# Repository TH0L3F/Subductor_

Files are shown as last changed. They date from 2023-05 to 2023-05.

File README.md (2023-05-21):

#Subductor

Une machine pour le laboratoire de sciences naturelles de L'université de Lille (Cité scientifique) SN5

## Objectif

Le subductor a pour objectif de subducter ... Bon c'est pas super clair comme ça donc je vais faire mieux:
L'objectif est de tirer un bloc de sable avec un tissus (ici un morceau de voile de bateau) par le dessous afin de simuler des mouvements tectoniques et leurs effets sur des blocs de sable.

### Matériel

Pour se faire est mis à la disposition de l'utilisateur un boitier possédant un écran lcd 4 lignes 20 caractères par lignes ainsi qu'un encodeur rotatif avec un bouton inclus.

### Préparation

Au démarrage de la machine il faut avec le mode Incrémental faire deux tours de aux tapis autour de la tige d'enroulement puis redemarrer la machine pour commencer à l'utiliser.
Le nombre d'enroulement du tapis n'étant pas mesurer : il s'agit de la seule manière de connaître sa position eu démarrage puis de la calculer au cours du fonctionnement de la machine.

### Mode

Dans un premier temps il faut choisir un mode entre:
-Continu : Sélection de la vitesse de déplacement du tapis.
-Incrémental : Sélection de la position voulue du tapis puis déplacement de celui-ci.

Pour passer d'un mode à l'autre il faut éteindre puis allumer la machine (Choix seulement au démarrage).

#### Continu

Choix de la vitesse avec l'encodeur puis appuie sur le bouton 2 secondes pour mettre en mouvement la machine.
Lors d'un changement de vitesse en bougeant l'encodeur il faut appuyer sur le bouton pour confirmer la modification et qu'elle devienne effective.

#### Incrémental

Choix de la position avec l'encodeur puis appuie sur le bouton 2 secondes pour mettre en mouvement la machine.
A chaques changement de position il faut appuyer à nouveau sur le bouton pendant 2 secondes sur le bouton de l'encodeur pour que le changement soit pris en compte.

## Electronique

Du point de vue électronique une carte permet de connecter chaques composants via des connecteurs JST-XH afin de limiter au maximum la possibilité de déconnexion dû aux vibrations ou au temps. Les composants sont tous connecter à un atmega328p cadencé à 16MHz. L'écran en I2C et l'encodeur sur des pin digital. Le driver de moteur pas à pas sur des pins digital lui aussi.

## Programmation

Pour programmer il faut utiliser un programmateur spécifique et le connecteur correspondant sur la carte. Le programmateur est le même que le programmateur du projet Slicor. Une petite fléche permet sur la carte et le connecteur du programmateur permet de détromper le sens de connexion. Ensuite via l'IDE arduino il est possible de mettre le bootloader ("carte : arduino uno", "programmateur : TINYasISP" puis "burn bootloader") il est nécessaire de mettre le bootloader si la puce n'en a pas déjà. Ensuite avec l'option "programmer via un programmateur" il est possible de téléverser le programmer dans le microcontrôleur. 

ATTENTION: Avec le programmeteur mis à dispositon une erreur survient dans certaine condition. Si un timeout est émis par le programmateur une solution est d'enlever ou d'ajouter des delay(1) dans la partie setup du programme. (Si une meilleure solution existe je suis preneur).

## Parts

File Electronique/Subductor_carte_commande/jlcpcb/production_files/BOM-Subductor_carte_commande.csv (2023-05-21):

Comment | Designator | Footprint | LCSC
16MHz | Y1 | Crystal_SMD_3225-4Pin_3.2x2.5mm | C13738
ATmega328-A | uC1 | TQFP-32_7x7mm_P0.8mm | C14877
22p | C3,C4 | C_0402_1005Metric | C1555
100k | R13 | R_1206_3216Metric | C17900
10k | R1,R2 | R_1206_3216Metric | C17902
Connecteur_Prog | J4 | PinHeader_1x08_P2.54mm_Vertical
Conn_encodeur_rotatif | J3 | JST_XH_B5B-XH-A_1x05_P2.50mm_Vertical
Connecteur_bouton_1 | J5 | JST_XH_B2B-XH-A_1x02_P2.50mm_Vertical
Connecteur_ecran | J2 | JST_XH_B4B-XH-A_1x04_P2.50mm_Vertical
Connecteur_Alim | J1 | TerminalBlock_bornier-2_P5.08mm
MountingHole_Pad | H1 | MountingHole_4.3mm_M4_DIN965_Pad
MountingHole_Pad | H4 | MountingHole_4.3mm_M4_DIN965_Pad
Connecteur_bouton_2 | J6 | JST_XH_B2B-XH-A_1x02_P2.50mm_Vertical
MountingHole_Pad | H3 | MountingHole_4.3mm_M4_DIN965_Pad
MountingHole_Pad | H2 | MountingHole_4.3mm_M4_DIN965_Pad
TestPoint | TP1 | TestPoint_Pad_1.5x1.5mm
Conn_01x03_Female | J7 | JST_XH_B3B-XH-A_1x03_P2.50mm_Vertical

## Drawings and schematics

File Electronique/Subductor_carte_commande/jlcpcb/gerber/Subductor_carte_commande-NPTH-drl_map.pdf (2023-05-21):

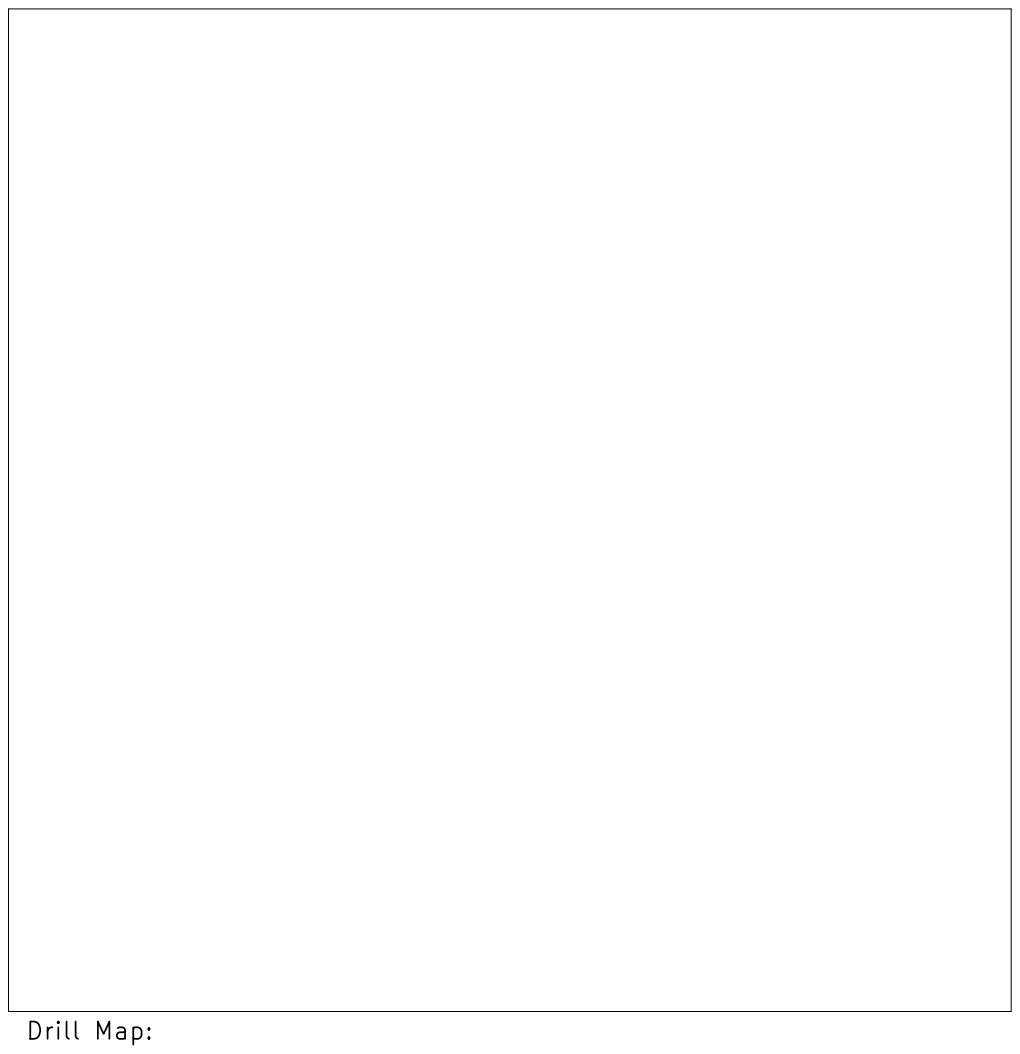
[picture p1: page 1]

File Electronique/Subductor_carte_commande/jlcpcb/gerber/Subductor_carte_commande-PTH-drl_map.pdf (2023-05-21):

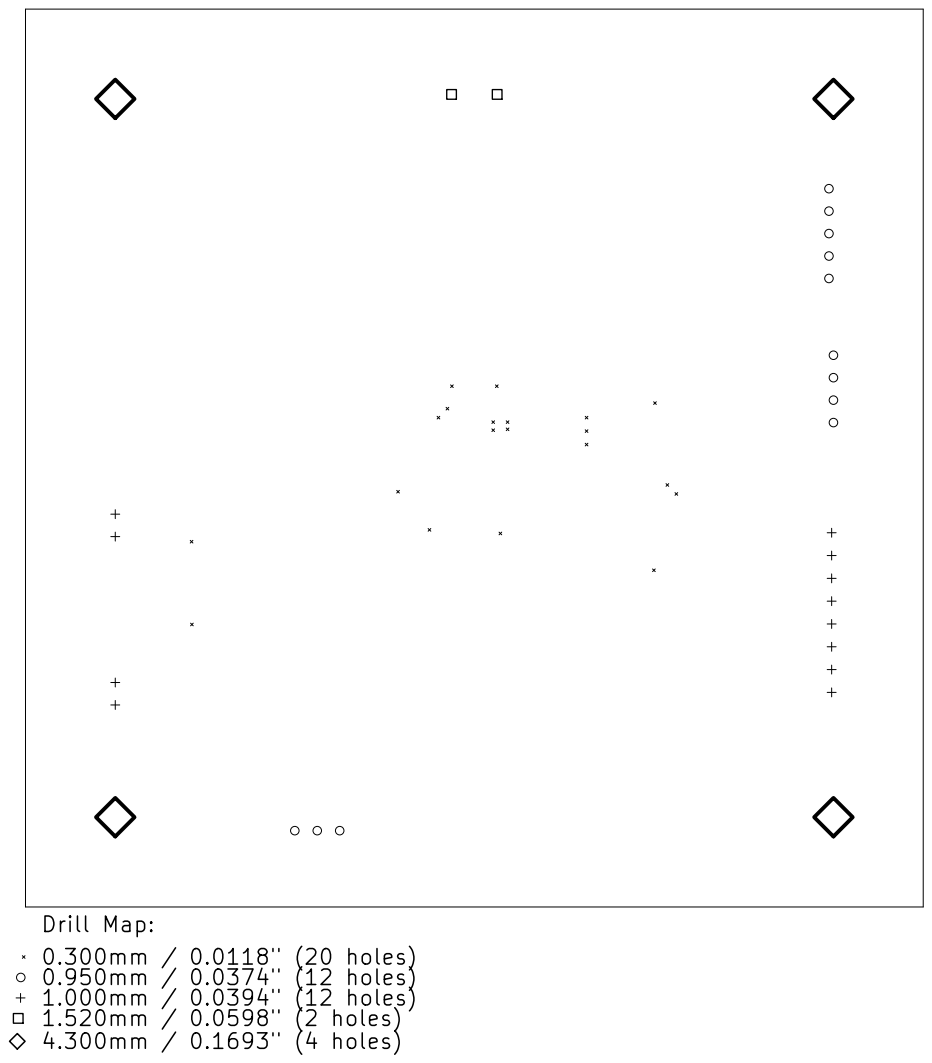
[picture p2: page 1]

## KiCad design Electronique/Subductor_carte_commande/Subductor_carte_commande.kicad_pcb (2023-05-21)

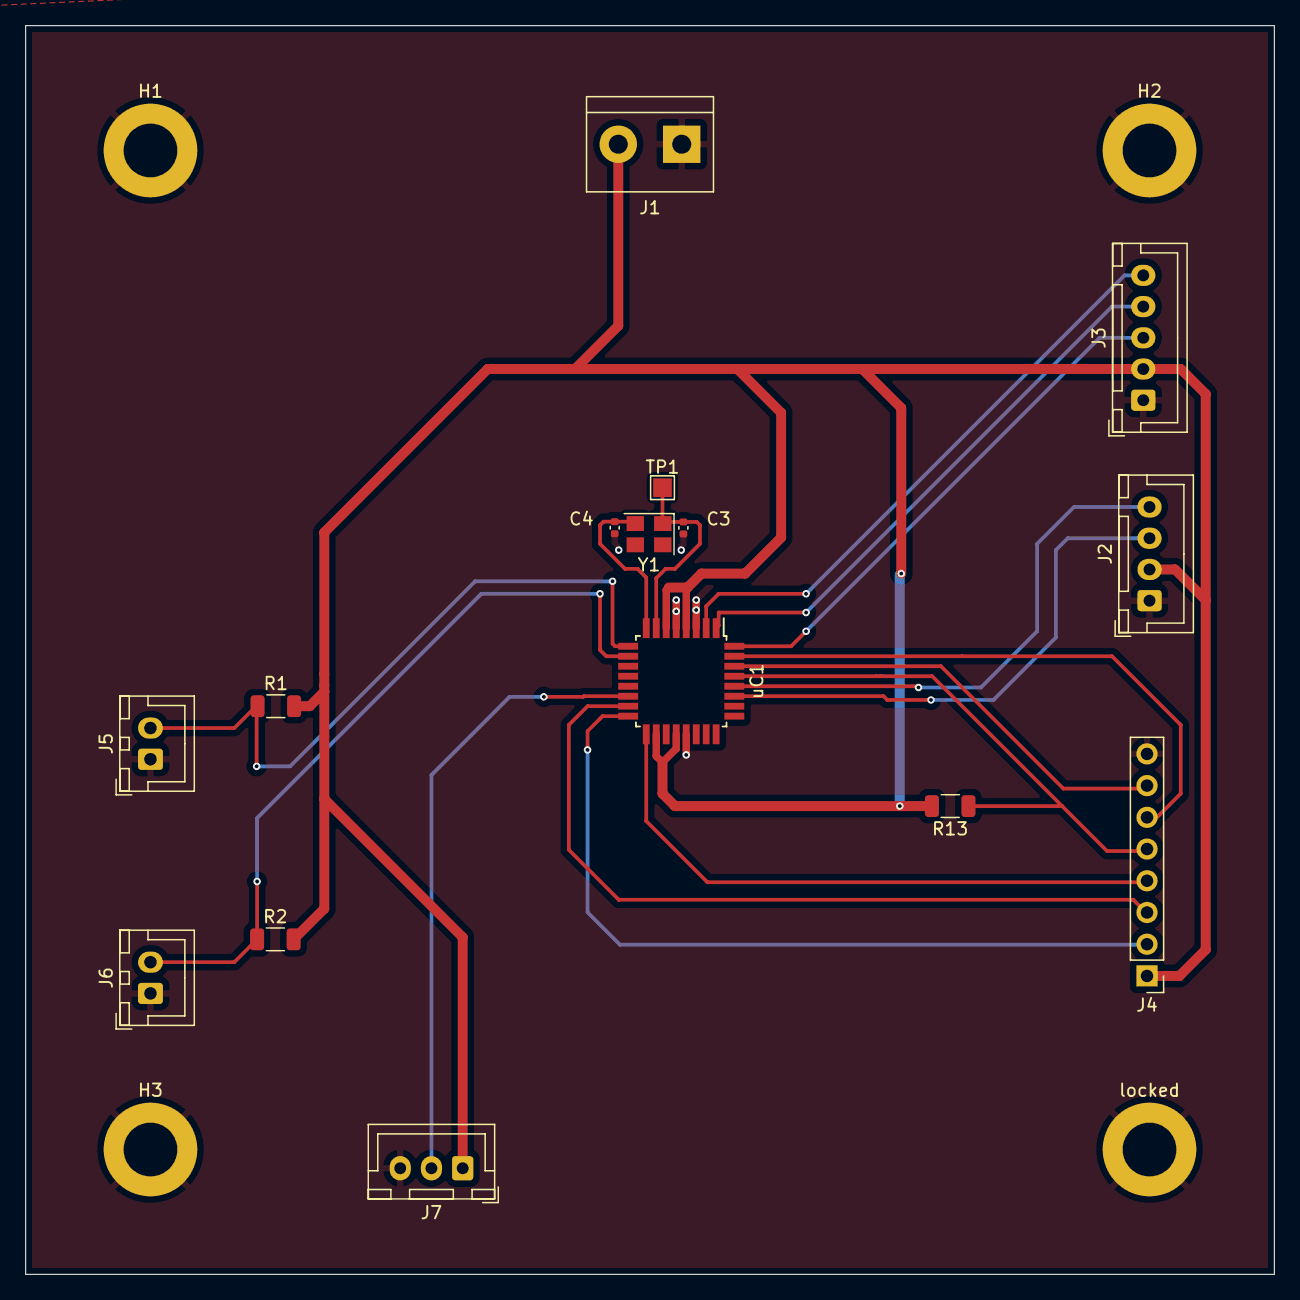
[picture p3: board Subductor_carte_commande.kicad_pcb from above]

Board: 4 copper layers, 100.0 x 100.0 mm, 19 parts (0 on the bottom side), 18 nets.

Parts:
C3, C4: 22p; C_0402_1005Metric
H1, H2, H3: MountingHole_Pad; MountingHole_4.3mm_M4_DIN965_Pad
J1: Connecteur_Alim; TerminalBlock_bornier-2_P5.08mm
J2: Connecteur_ecran; JST_XH_B4B-XH-A_1x04_P2.50mm_Vertical
J3: Conn_encodeur_rotatif; JST_XH_B5B-XH-A_1x05_P2.50mm_Vertical
J4: Connecteur_Prog; PinHeader_1x08_P2.54mm_Vertical
J5: Connecteur_bouton_1; JST_XH_B2B-XH-A_1x02_P2.50mm_Vertical
J6: Connecteur_bouton_2; JST_XH_B2B-XH-A_1x02_P2.50mm_Vertical
J7: Conn_01x03_Female; JST_XH_B3B-XH-A_1x03_P2.50mm_Vertical
R1, R2: 10k; R_1206_3216Metric
R13: 100k; R_1206_3216Metric
TP1: TestPoint; TestPoint_Pad_1.5x1.5mm
Y1: 16MHz; Crystal_SMD_3225-4Pin_3.2x2.5mm
locked: MountingHole_Pad; MountingHole_4.3mm_M4_DIN965_Pad
uC1: ATmega328-A; TQFP-32_7x7mm_P0.8mm

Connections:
+5V: J1.2, J2.2, J3.2, J4.1, J7.1, R1.2, R2.2, R13.2, uC1.4 (VCC), uC1.6 (VCC), uC1.18 (AVCC), uC1.20 (AREF)
BUZZER: J7.2, uC1.14 (PB2)
Bouton1: J5.2, R1.1, uC1.9 (PD5)
Bouton2: J6.2, R2.1, uC1.10 (PD6)
CLK: J3.5, uC1.2 (PD4)
DT: J3.4, uC1.1 (PD3)
GND: C3.2, C4.2, H1.1, H2.1, H3.1, J1.1, J2.1, J3.1, J4.8, J5.1, J6.1, J7.3, locked.1, uC1.3 (GND), uC1.5 (GND), uC1.21 (GND)
MISO: J4.2, uC1.16 (PB4)
MOSI: J4.3, uC1.15 (PB3)
unnamed: C3.1, TP1.1, Y1.1, uC1.7 (XTAL1/PB6)
unnamed: C4.1, Y1.2, uC1.8 (XTAL2/PB7)
RST: J4.5, R13.1, uC1.29 (~RESET/PC6)
SCK: J4.4, uC1.17 (PB5)
SCL: J2.4, uC1.28 (PC5)
SDA: J2.3, uC1.27 (PC4)
SW: J3.3, uC1.32 (PD2)
UART RX: J4.7, uC1.30 (PD0)
UART TX: J4.6, uC1.31 (PD1)

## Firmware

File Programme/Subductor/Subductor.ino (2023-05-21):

/*
Software by TH0L3F
*/

//Utilitaire pour l'écran LCD
#include <Wire.h> 
#include <LiquidCrystal_I2C.h>
#define len_lcd 20 //Nombre de caractère en longueur de l'écran
#define high_lcd 4 //Nombre de lignes de l'écran
#define lcd_adress 0x27 //Adresse de l'écran
LiquidCrystal_I2C lcd(lcd_adress,len_lcd,high_lcd);  //Configurer l'écran 
bool screen_refresh = false;

//Encodeur rotatif KY-040
//Parameters
#define CLK 2
#define DT 3
#define SW 4
int counter = 0;
bool pos_chng = 0;
unsigned long old_pos = 0; //Ancienne position du tapis en dizieme de um
unsigned long new_pos = 0; //Nouvelle position du tapis en dizieme de um
bool ax = false; //Ancien état de la broche A
bool bx = false; //Ancien état de la broche B
bool a = false; //Nouvel état de la broche A
bool b = false; //Nouvel état de la broche B
bool btn = 0;
bool abtn = 0;
unsigned long t1 = 0;
unsigned long t2 = 0;
unsigned long t3 = 0;

//Buzzer
#define pin_buzzer 10

//Driver stepper
#define DR_step 5 //Broche d'impulsion pour chaques pas
#define DR_dir 6 //Broche de sélection de la direction
const long step_per_revolution = 800; // Nombre de par par révolution du moteur pas à pas
const long init_r = 180000; //rayon initial de l'axe d'enroulement en en dizieme de um
const long red = 100; //Coefficient de réduction du moteur
long step_per_rev_red = step_per_revolution*red; //Nombre de pas du moteur pour faire un tour en sortie du réducteur
long e = 4000; //Epaisseur du tissus en en dizieme de um
long n_step_f = 0;//Enregistre le nombre de pas effectuer depuis le début du tour actuel
long n_tour = 2;//Enregistre le nombre de tour effectuer depuis le démarrage de la machine
unsigned long mm_step = 0;//Permet de sauvegarder le nombre de dizieme de um effectuer à chaques pas.
long pi =  31415; //Pi en dizieme de um
long delay_step = 100; //Temps d'attente entre deux pas.

//Choix de mode
bool mode = 0;  //Permet de sauvegarder le mode choisie au démarrage
                //0 mode incrémental
                //1 mode continue
int sel;//Sauvegarde de la position en cours
char c1;//Affichage du choix 
char c2;//Affichage du choix
char c3;//Affichage du choix

//Mode continue
#define v1 5 //5mm/h
#define v2 10 //10mm/h
int vitesse = 0; //Vitesse choisir au démarrage

void setup(){
  //Configurer l'éc&ran LCD
  lcd.init();  //initialize the lcd
  lcd.backlight();  //open the backlight 

  pinMode(CLK, INPUT_PULLUP);
  pinMode(DT, INPUT_PULLUP);
  attachInterrupt(digitalPinToInterrupt(CLK), readRotary, CHANGE);
  attachInterrupt(digitalPinToInterrupt(DT), readRotary, CHANGE);

  pinMode(SW, INPUT_PULLUP);

  pinMode(pin_buzzer, OUTPUT);

  pinMode(DR_step, OUTPUT);
  pinMode(DR_dir, OUTPUT);
  mm_step = (((e*n_tour+init_r)/red)*2*pi)/step_per_revolution/1000;

  //Affichage au démarrage
  screen(mode);
  delay(2000);
  screen(1);

  delay(1);
  delay(1);
  delay(1);
  delay(1);
  delay(1);
  delay(1);
  delay(1);
  delay(1);

}

void loop(){
  if(screen_refresh){
    screen(mode); //Mise à jour de l'écran
    screen_refresh = false;
  }
  if(pos_chng){
    if((mode == 2) || (mode == 3)){
      new_pos = (counter/4)*100000;
    }
    else if(mode == 1){
      sel = (counter/4)%3;
    }
    pos_chng = 0;
    screen_refresh = 1;

  }
  button();//Permet de récupérer les infos sur le bouton et d'executer les actions associés.
}

void button(){
  btn = digitalRead(SW);
  if((mode == 3)||(mode == 2)){
    if(abtn == HIGH && btn == LOW){       // bouton appuyé
      t1 = millis();//t1 le temps horloge au début de l'appuie
    }
    else if(abtn == LOW && btn == HIGH) { // bouton relaché
      t2 = millis();//t2 le temps horloge à la fin de l'appuie
      long t3 = t2 - t1; //t3 le temps appuyès du bouton
      if(t3 > 1000){
        //Le bouton a été appuyé pendant plus d'une seconde.
        move();
        screen_refresh = 1;
      }
    }
  }
  else if(mode == 1){
    if(sel == 0){
      mode = 2;
    }
    else {
      mode = 3;
      if(sel == 1){
        vitesse = v1;
      }
      else{
        vitesse = v2;
      }
    }
    screen_refresh = 1;
  }
  // enregistre le dernier état
  abtn = btn;
}

void move(){
  //Permet de faire le déplacement entre la position voulue et la position actuelle
  //Ce programme fait une approximation qui est de considérer que l'enroulement ce fait en suivant la règle suivante:
  //Chaque tour de film augmente le diamètre de l'axe d'enroulement de 2 fois e pour l'enroulement suivant.

  if(mode == 2){
    while(old_pos < new_pos){//Tant que la position n'est pas atteinte on bouge

      //Calcul du déplacement en fonction du nombre de tours effectués
      if(n_step_f > step_per_rev_red-1){
        //Si on vient de finir un tour on recalcul le nombre de pas à effectuer pour le suivant
        n_tour++;
        mm_step = (((e*n_tour+init_r)/red)*2*pi)/step_per_revolution/1000;
        n_step_f = 0;
        delay_step = vitesse/mm_step;//Calcul du nouveau délai par pas pour obtenir une vitesse continue
        delay(100);
      }
      //On fait un pas
      digitalWrite(DR_step,HIGH);
      delayMicroseconds(delay_step);//Petite pause entre chaques pas pour limiter la vitesse de rotation et donc de déplacement du moteur.
      digitalWrite(DR_step,LOW);
      delayMicroseconds(delay_step);//Petite pause entre chaques pas pour limiter la vitesse de rotation et donc de déplacement du moteur.
      old_pos += mm_step;//On enregistre la nouvelle position
      n_step_f++;
    }
  }
  else if(mode == 3){
    while(1){
      //Calcul du déplacement en fonction du nombre de tours effectués
      if(n_step_f > step_per_rev_red-1){
        //Si on vient de finir un tour on recalcul le nombre de pas à effectuer pour le suivant
        n_tour++;
        mm_step = (((e*n_tour+init_r)/red)*2*pi)/step_per_revolution/1000;
        n_step_f = 0;
        delay(100);
      }
      //On fait un pas
      digitalWrite(DR_step,HIGH);
      delayMicroseconds(delay_step);//Petite pause entre chaques pas pour limiter la vitesse de rotation et donc de déplacement du moteur.
      digitalWrite(DR_step,LOW);
      delayMicroseconds(delay_step);//Petite pause entre chaques pas pour limiter la vitesse de rotation et donc de déplacement du moteur.
      old_pos += mm_step;//On enregistre la nouvelle position
      n_step_f++;
    }
  }
}

void screen(int mode){
  delay(1);
  if(mode == 0){ //Ecran de démarrage
    lcd.setCursor(0,0);//On remet le curseur en haut à gauche
    lcd.clear();//On efface l'écran avant d'afficher de nouvelles informations
    affichage(0,"Subductor en cours",1);
    affichage(1,"de demarrage.",1);
    affichage(2,"Patientez...",1);
    affichage(3,"Fait par TH0L3F",1);
  }
  else if(mode == 1){
    lcd.setCursor(0,0);//On remet le curseur en haut à gauche
    lcd.clear();//On efface l'écran avant d'afficher de nouvelles informations
    affichage(0,"Choix du mode",2);
    if (sel == 0){ //Curseur sur choix 1
      c1 = "*";
      c2 = "";
      c3 = "";
    }
    else if(sel == 1){ //Curseur sur choix 2
      c1 = "";
      c2 = "*";
      c3 = "";
    } 
    else if(sel == 2){ //Curseur sur choix 3
      c1 = "";
      c2 = "";
      c3 = "*";
    }
    affichage(1,c1 + " Mode incrémental" ,2);
    affichage(2,c2 + " Mode continue " + String(v1) ,2);
    affichage(2,c3 + " Mode continue " + String(v2) ,2);
  }
  else if(mode == 2){ //Ecran mode incrémental
    lcd.setCursor(0,0);//On remet le curseur en haut à gauche
    lcd.clear();//On efface l'écran avant d'afficher de nouvelles informations
    affichage(0,"Position",2);
    affichage(1,"old : " + String(old_pos/(100000))+" mm",2);
    affichage(2,"new : " + String(new_pos/(100000))+" mm",2);
    affichage(3,String((float)mm_step/100.0)+" um/step",2);//100
  }
  else if(mode == 3){ //Ecran mode continue
    lcd.setCursor(0,0);//On remet le curseur en haut à gauche
    lcd.clear();//On efface l'écran avant d'afficher de nouvelles informations
    affichage(0,"Vitesse",2);
    affichage(1, String(vitesse)+"mm/h",2);
    affichage(3, String((float)mm_step/100.0)+" um/step",2);//100
  }
}

void affichage(int ligne, String text, int type){
  if(type == 1){ //Affichage du texte au centre de la ligne
    lcd.setCursor ( int(len_lcd/2)-int(text.length()/2), ligne ); 
    lcd.print(text); 
  }
  else if(type == 2){//Affichage aligner à gauche
    lcd.setCursor ( 0, ligne);
    lcd.print(text);
  }
  else if(type == 2){//Affichage aligner à droite
    lcd.setCursor ((len_lcd - text.length()), ligne);
    lcd.print(text);
  }
  return;
}

void readRotary(){
  a = digitalRead(CLK);
  b = digitalRead(DT);
  if(ax == a && bx == b){return ;}//Pas de mouvements
  else if(ax && bx && !a && b){counter++;}//Mouvement dans le sens 1
  else if(!ax && bx && !a && !b){counter++;}//Mouvement dans le sens 1
  else if(!ax && !bx && a && !b){counter++;}//Mouvement dans le sens 1
  else if(ax && !bx && a && b){counter++;}//Mouvement dans le sens 1
  else if(ax && bx && a && !b){counter--;}//Mouvement dans le sens 2
  else if(ax && !bx && !a && !b){counter--;}//Mouvement dans le sens 2
  else if(!ax && !bx && !a && b){counter--;}//Mouvement dans le sens 2
  else if(!ax && bx && a && b){counter--;}//Mouvement dans le sens 2
  else{}//Il y a eu un saut d'un état
  if(counter < 0){
    counter = 0;
  }
  ax = a;//Sauvegarde des nouveaux paramètres
  bx = b;//Sauvegarde des nouveaux paramètres
  pos_chng = 1;
}

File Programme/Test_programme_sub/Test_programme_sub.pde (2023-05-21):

const float step_per_revolution = 800.0; // Nombre de par par révolution du moteur pas à pas
const float init_D = 35.0; //Diametre initial de l'axe d'enroulement
const float red = 100.0; //Coefficient de réduction du moteur
const float e = 0.3; //Epaisseur du tissus
int n_step_f = 0;//Enregistre le nombre de pas effectuer depuis le début du tour actuel
int n_tour = 2;//Enregistre le nombre de tour effectuer depuis le démarrage de la machine
float mm_step = 0;//Permet de sauvegarder le nombre de mm effectuer à chaques pas.
float pi =  3.14159265359;

int counter = 0;
bool pos_chng = 0;
float old_pos = 0;
float act_pos = 0;
float new_pos = 0;

while(old_pos < new_pos){//Tant que la position n'est pas atteinte on bouge
  //Calcul du déplacement en fonction du nombre de tours effectués
  if(n_step_f > (int)(step_per_revolution*red)){
    //Si on vient de finir un tour on recalcul le nombre de pas à effectuer pour le suivant
    n_tour++;
    mm_step = (2*pi*(e*n_tour+init_D/2))/(step_per_revolution*red);
    n_step_f = 0;
  }
  n_step_f++;
}
